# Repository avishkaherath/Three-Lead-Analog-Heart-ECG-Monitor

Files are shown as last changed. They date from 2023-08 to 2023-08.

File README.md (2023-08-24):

# Three-Lead-Analog-Heart-ECG-Monitor
A heart ECG monitor is a device that provides real-time electrical measurements of the heart's activity, aiding in diagnosing cardiac conditions like arrhythmias. This non-invasive method utilizes a 3-lead ECG signal acquired through electrodes placed on the left shoulder, right shoulder, and lower left abdomen. To enhance signal quality, noise reduction is performed using an instrumentation amplifier. Additionally, interference from 50Hz power supply noise is mitigated using a notch filter.

After noise reduction, the signal undergoes further refinement through a low-pass filter (cut-off frequency: 150Hz) and a high-pass filter (cut-off frequency: 0.05Hz). These filters isolate the essential cardiac signal while eliminating unwanted frequencies. The resulting filtered ECG signal is then amplified and displayed on an oscilloscope, enabling healthcare professionals to observe the heart's electrical activity.

## ECG Monitor
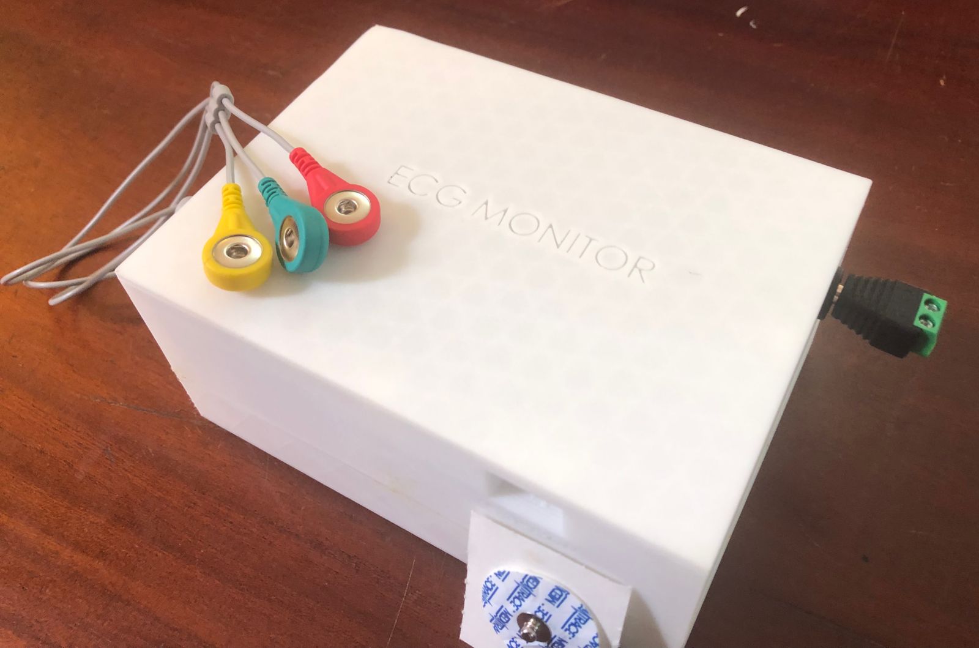
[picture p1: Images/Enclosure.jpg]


## Output ECG Waveform
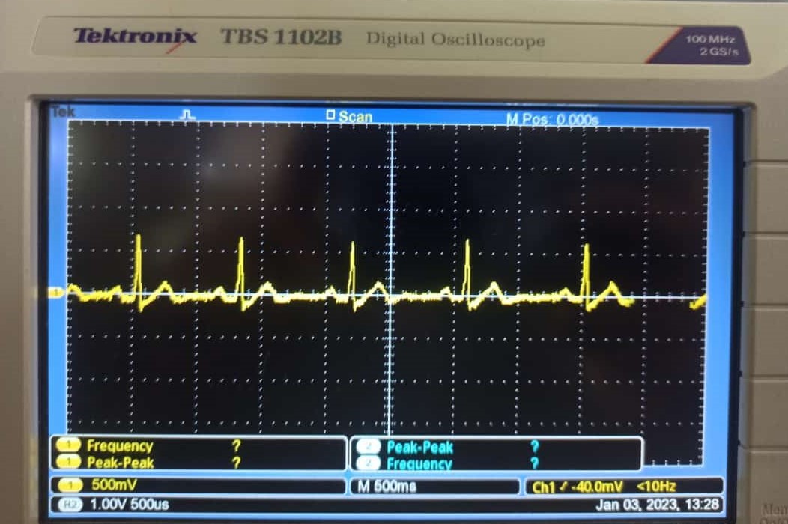
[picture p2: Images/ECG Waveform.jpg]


## Internal View
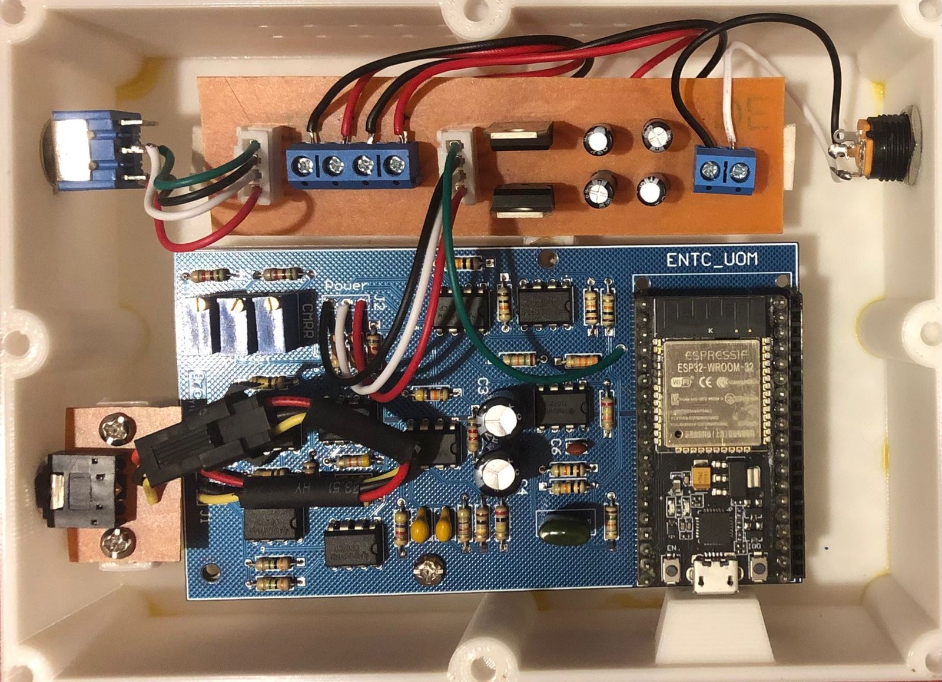
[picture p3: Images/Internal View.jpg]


## PCB Design
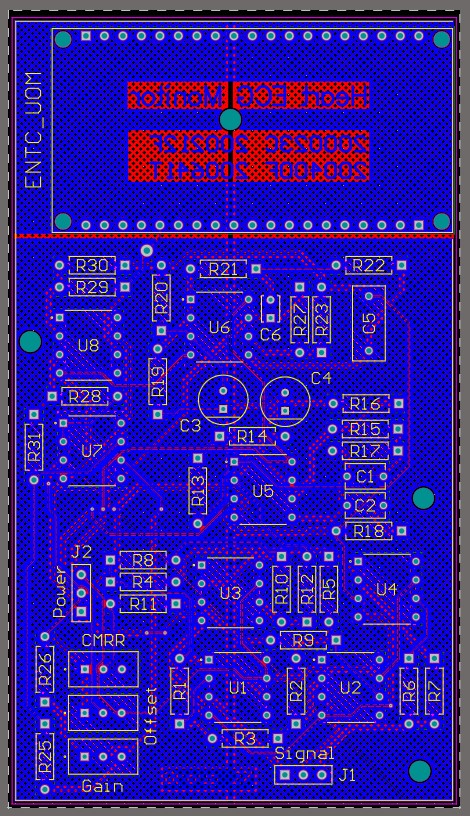
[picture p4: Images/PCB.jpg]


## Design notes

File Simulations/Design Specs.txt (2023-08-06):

Filter		Lower cutoff		Upper cutoff		Gain				Order

Notch			39.941 Hz			62.0634 Hz			1				2

HPF			68.3582 mHz			-				1				2

LPF			-				147.678 Hz			2				2

%%%%%%%%%%%%%%%%%%%%%%%%%%%%%%%%%%%%%%%%%%%%%%%%%%%%%%%%%%%%%%%%%%%%%%%%%%%%%%%%%%%%%%%%%%%%%%%%%%%%%%%%%%%%%%%%%%%%%%%%%%%%%%%%%%%%%%

Instrumentation Differential Mode						110

Instrumentation Common Mode							2.38407e-006

Summing Amplifier							min - 1.04853	max - 21.603

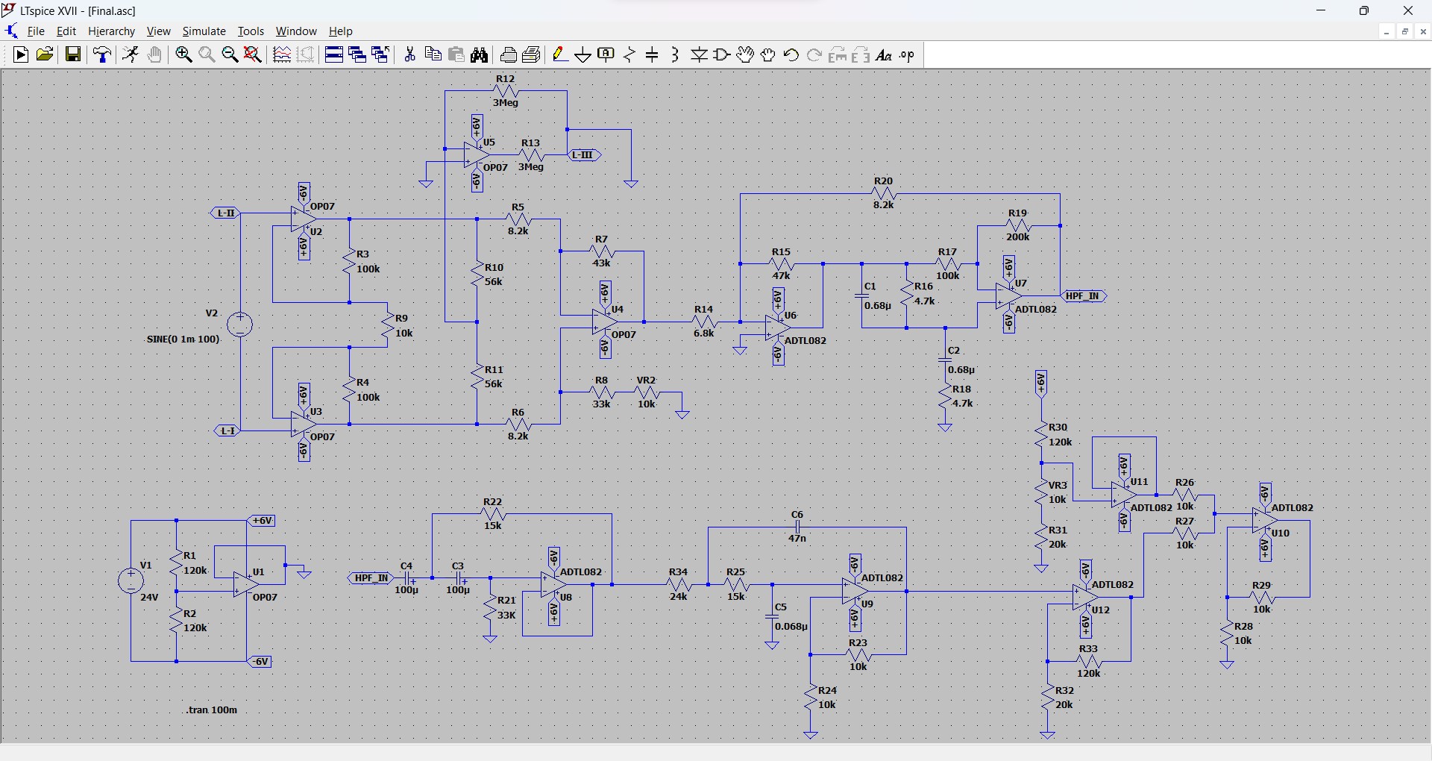
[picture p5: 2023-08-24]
Images/Schematic.jpg

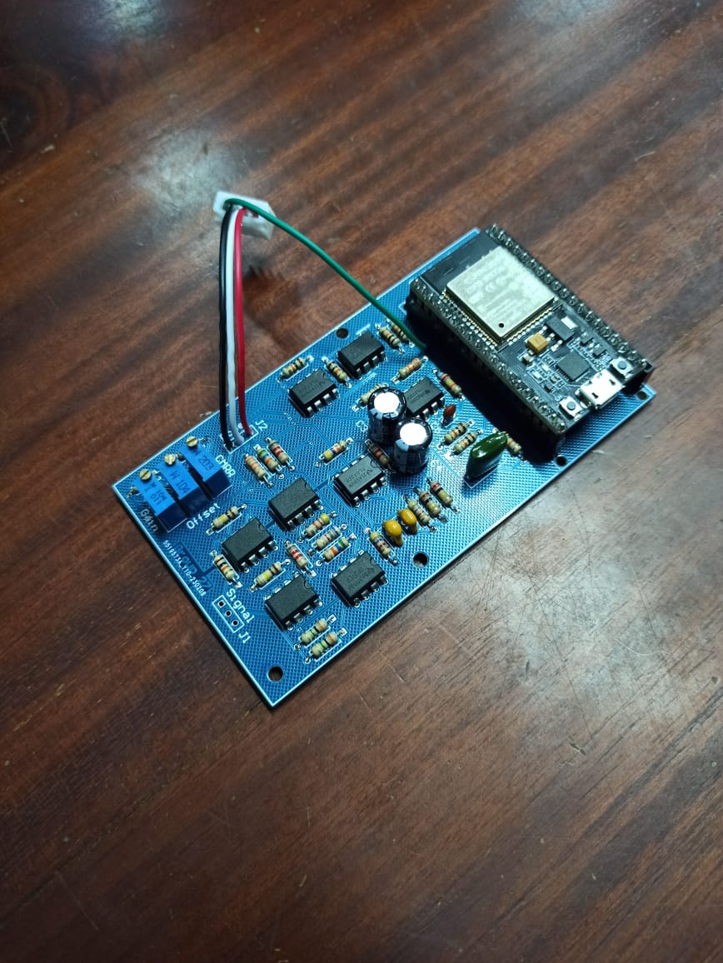
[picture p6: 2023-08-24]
Images/Final PCB.jpg

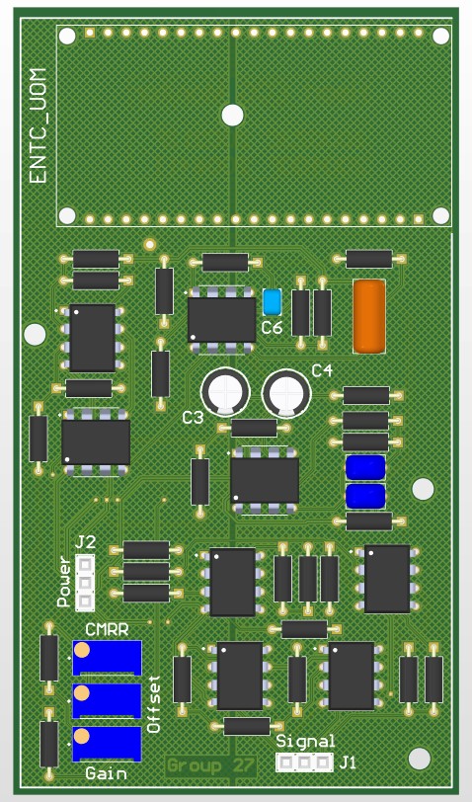
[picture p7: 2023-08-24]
Images/PCB_3D.jpg

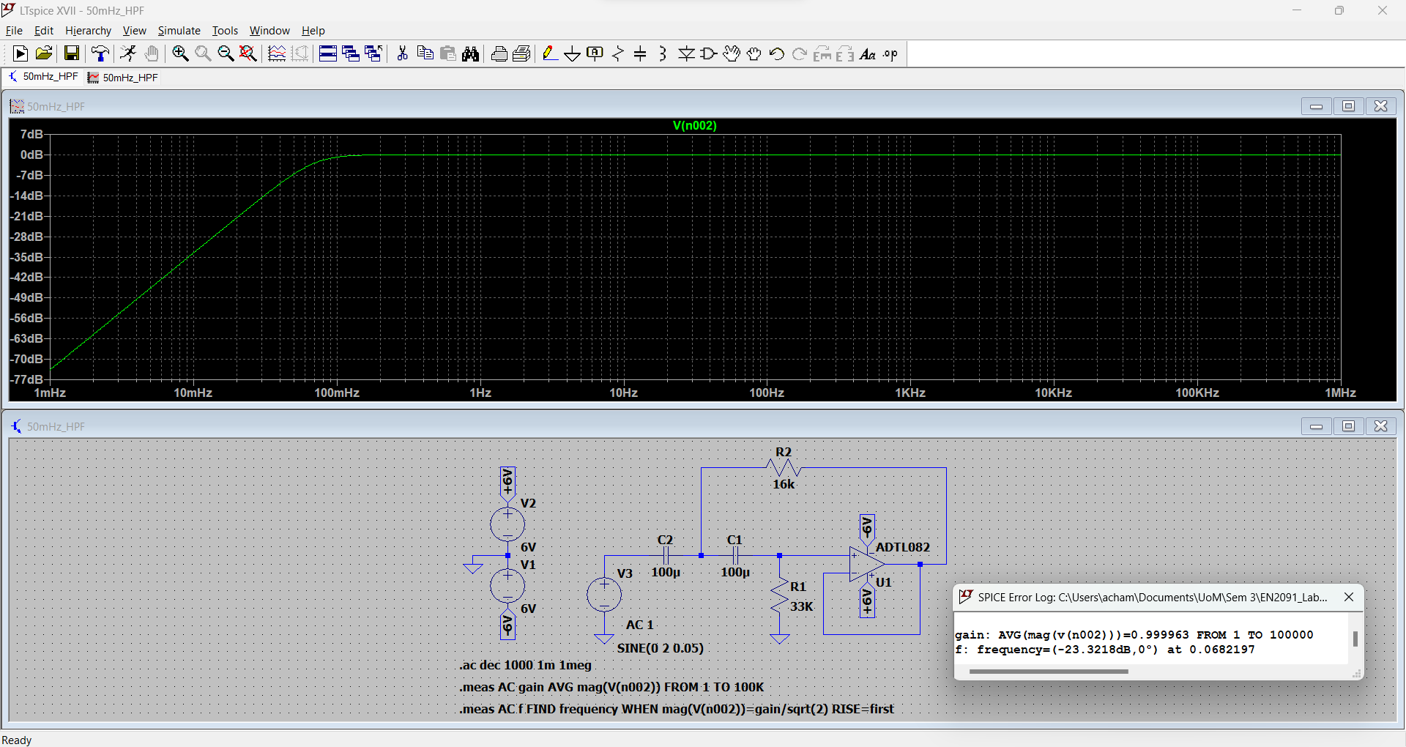
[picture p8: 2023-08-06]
Simulations/Screenshots/HPF.png

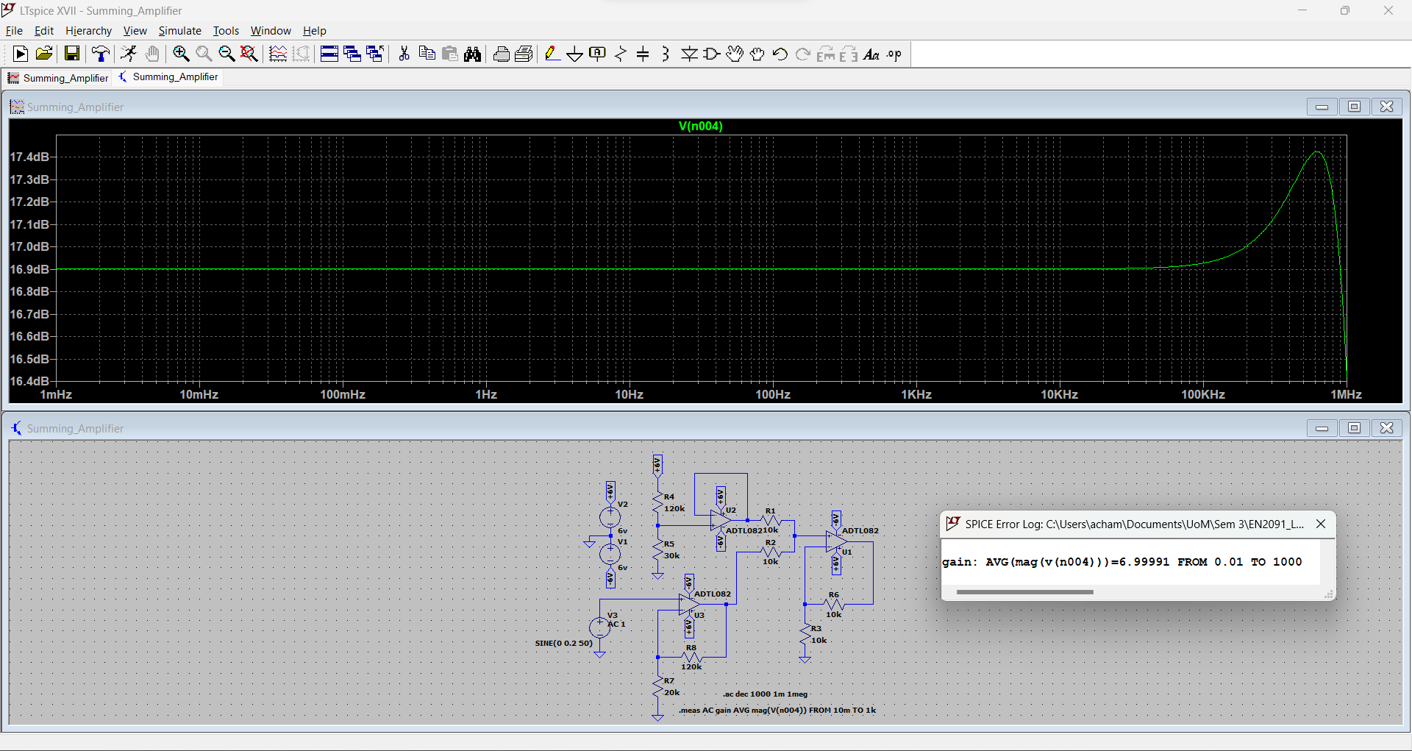
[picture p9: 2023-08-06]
Simulations/Screenshots/Summing_Amplifier.png

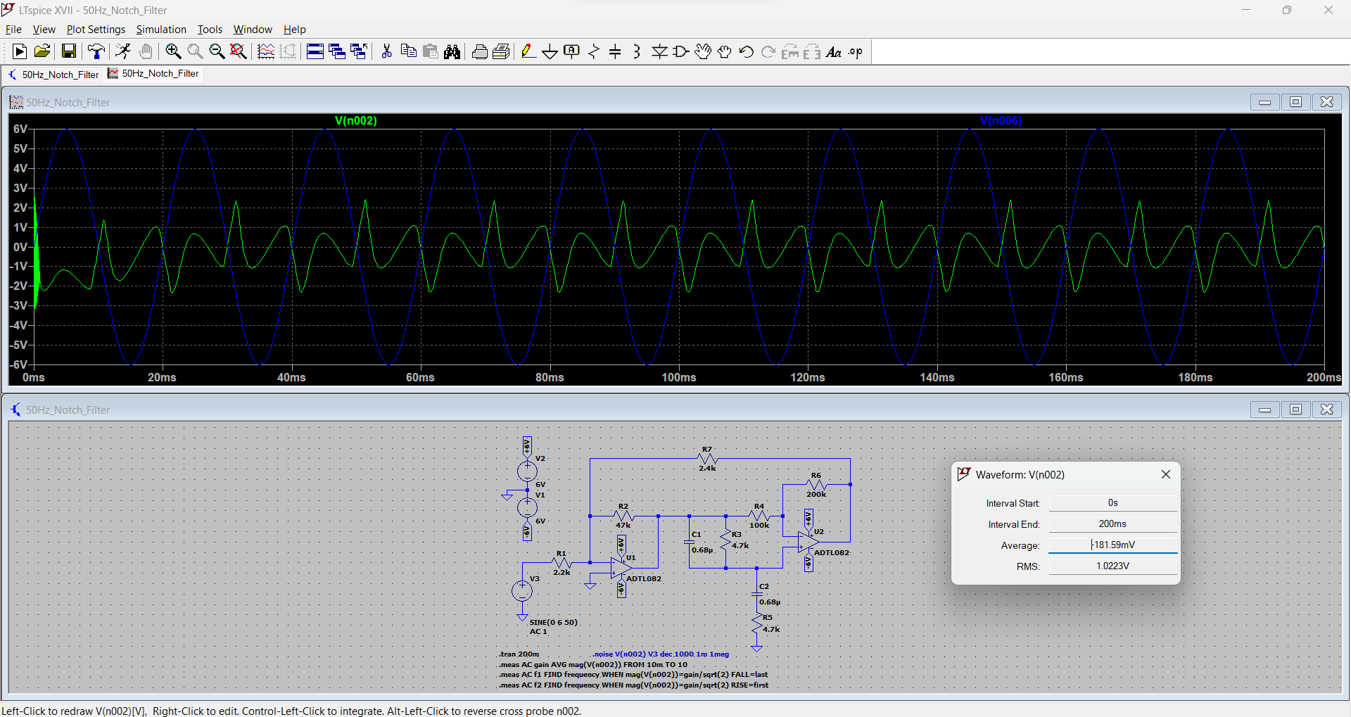
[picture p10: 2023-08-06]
Simulations/Screenshots/Notch_Filter_6V.png

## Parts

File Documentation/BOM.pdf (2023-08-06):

## Heart ECG Monitor Group 27

## BILL OF MATERIAL

Item | Quantity | Price (Rs.)
Resistors | 85 | 325.00
Capacitors | 10 | 253.50
Potentiometer | 1 | 142.00
Breadboard | 2 | 980.00
Variable Resistor | 1 | 50.00
40 pin Male Headers | 1 | 230.00
Rocker Switch | 1 | 18.00
Heat Shrink Tube | 1 | 24.00
Toggle Switch | 1 | 100.00
Connectors | | 350.00
OpAmp | 8 | 745.00
PCB | 3 | 4350.00
ECG Sensor | 1 | 1800.00
Audio Jack | 1 | 100.00
Wire Kit | 1 | 500.00
Enclosure | 1 | 8850.00
Screws | 15 | 75.00
Total | | 18892.50

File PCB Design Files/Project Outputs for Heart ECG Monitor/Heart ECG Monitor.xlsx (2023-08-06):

Comment | Description | Designator | Footprint | LibRef | Quantity
0.68uF |  | C1, C2 | CAPRB500W50L550T350H600 | FA26NP02J472JNU06 | 2
100uF | Cap Aluminum Lytic 100uF 25V 20% (6.3 X 11.2mm) Radial 2.5mm 130mA 1000h 105°C Ammo Pack | C3, C4 | FP-RAD-TH-D_6_3_0_5-L_11-MFG | CMP-001-00083-1 | 2
68nF |  | C5 | CAPRR750W60L1030T450H750 | ECQE2683JF | 1
47nF | Cap Ceramic 470pF 50V C0G 5% Radial 2.5mm 125°C Ammo Pack | C6 | FP-RCE0DB-MFG | CMP-001-00084-1 | 1
10uF | Cap Aluminum Lytic 100uF 25V 20% (6.3 X 11.2mm) Radial 2.5mm 130mA 1000h 105°C Ammo Pack | CM1, CM3 | FP-RAD-TH-D_6_3_0_5-L_11-MFG | CMP-001-00083-1 | 2
1uF | Cap Aluminum Lytic 100uF 25V 20% (6.3 X 11.2mm) Radial 2.5mm 130mA 1000h 105°C Ammo Pack | CM2, CM4 | FP-RAD-TH-D_6_3_0_5-L_11-MFG | CMP-001-00083-1 | 2
SIGNAL_IN | Low Profile Socket Strips, Through-hole, Vertical, -55 to 125 degC, 2.54 mm Pitch, 3-Pin, Female, RoHS | J1 | SMTC-SLW-103-01-X-S | CMP-1023-00128-1 | 1
POWER_IN | Low Profile Socket Strips, Through-hole, Vertical, -55 to 125 degC, 2.54 mm Pitch, 3-Pin, Female, RoHS | J2 | SMTC-SLW-103-01-X-S | CMP-1023-00128-1 | 1
3.5mm JACK | Conn 3.5MM Stereo Jack F 5 POS Solder RA Thru-Hole 5 Terminal 1 Port | Jin1 | SWITCHCRAFT_35RAPC4BHN2 | 35RAPC4BHN2 | 1
SIGNAL | Low Profile Socket Strips, Through-hole, Vertical, -55 to 125 degC, 2.54 mm Pitch, 3-Pin, Female, RoHS | Jin2 | SMTC-SLW-103-01-X-S | CMP-1023-00128-1 | 1
BATTERY |  | JM1 | CUI_TB001-500-04BE | TB001-500-04BE | 1
SWITCH | Low Profile Socket Strips, Through-hole, Vertical, -55 to 125 degC, 2.54 mm Pitch, 4-Pin, Female, RoHS | JM2 | SMTC-SLW-104-01-X-S | CMP-1023-00130-1 | 1
MAIN | Low Profile Socket Strips, Through-hole, Vertical, -55 to 125 degC, 2.54 mm Pitch, 4-Pin, Female, RoHS | JM3 | SMTC-SLW-104-01-X-S | CMP-1023-00130-1 | 1
OSCILLOSCOPE |  | JM4 | CUI_TB001-500-02BE | TB001-500-02BE | 1
100k | Axial Resistor, 100 KOhm, +/- 1%, 0.25 W, -55 to 155 degC, 2-Pin THD, RoHS, Bulk, Axial Resistor, 47.5 Ohm, +/- 1%, 0.25 W, -55 to 155 degC, 2-Pin THD, RoHS, Bulk | R1, R2, R15 | RESA60-630X240 | CMP-009-00045-4, CMP-009-00058-4 | 3
10k | Axial Resistor, 10 KOhm, +/- 1%, 0.25 W, -55 to 155 degC, 2-Pin THD, RoHS, Bulk | R3, R23, R27, R28, R29, R30, R31 | RESA60-630X240 | CMP-009-00047-4 | 7
56k | Axial Resistor, 47.5 KOhm, +/- 1%, 0.25 W, -55 to 155 degC, 2-Pin THD, RoHS, Bulk | R4, R5 | RESA60-630X240 | CMP-009-00057-4 | 2
3M | Axial Resistor, 1 MOhm, +/- 1%, 250 mW, -55 to 155 degC, 2-Pin THD, RoHS, Bulk | R6, R7 | RESA60-630X240 | CMP-009-00049-4 | 2
8.2k | Axial Resistor, 4.75 KOhm, +/- 1%, 0.25 W, -55 to 155 degC, 2-Pin THD, RoHS, Bulk, Axial Resistor, 47.5 Ohm, +/- 1%, 0.25 W, -55 to 155 degC, 2-Pin THD, RoHS, Bulk | R8, R9, R14 | RESA60-630X240 | CMP-009-00059-4, CMP-009-00058-4 | 3
43k | Axial Resistor, 47.5 KOhm, +/- 1%, 0.25 W, -55 to 155 degC, 2-Pin THD, RoHS, Bulk | R10 | RESA60-630X240 | CMP-009-00057-4 | 1
33k | Axial Resistor, 47.5 KOhm, +/- 1%, 0.25 W, -55 to 155 degC, 2-Pin THD, RoHS, Bulk, Axial Resistor, 47.5 Ohm, +/- 1%, 0.25 W, -55 to 155 degC, 2-Pin THD, RoHS, Bulk | R11, R20 | RESA60-630X240 | CMP-009-00057-4, CMP-009-00058-4 | 2
6.8k | Axial Resistor, 47.5 Ohm, +/- 1%, 0.25 W, -55 to 155 degC, 2-Pin THD, RoHS, Bulk | R12 | RESA60-630X240 | CMP-009-00058-4 | 1
47k | Axial Resistor, 47.5 Ohm, +/- 1%, 0.25 W, -55 to 155 degC, 2-Pin THD, RoHS, Bulk | R13 | RESA60-630X240 | CMP-009-00058-4 | 1
200k | Axial Resistor, 47.5 Ohm, +/- 1%, 0.25 W, -55 to 155 degC, 2-Pin THD, RoHS, Bulk | R16 | RESA60-630X240 | CMP-009-00058-4 | 1
4.7k | Axial Resistor, 47.5 Ohm, +/- 1%, 0.25 W, -55 to 155 degC, 2-Pin THD, RoHS, Bulk | R17, R18 | RESA60-630X240 | CMP-009-00058-4 | 2
15k | Axial Resistor, 47.5 Ohm, +/- 1%, 0.25 W, -55 to 155 degC, 2-Pin THD, RoHS, Bulk, Axial Resistor, 10 KOhm, +/- 1%, 0.25 W, -55 to 155 degC, 2-Pin THD, RoHS, Bulk | R19, R22 | RESA60-630X240 | CMP-009-00058-4, CMP-009-00047-4 | 2
24k | Axial Resistor, 10 KOhm, +/- 1%, 0.25 W, -55 to 155 degC, 2-Pin THD, RoHS, Bulk | R21 | RESA60-630X240 | CMP-009-00047-4 | 1
5.1k | Axial Resistor, 10 KOhm, +/- 1%, 0.25 W, -55 to 155 degC, 2-Pin THD, RoHS, Bulk | R25, R26 | RESA60-630X240 | CMP-009-00047-4 | 2
OP07CP |  | U1, U2, U3, U4, U8 | DIP794W45P254L959H508Q8 | OP07CP | 5
TL072BCP | Dual low-noise JFET-input low offset operational amplifier 8-PDIP 0 to 70 | U5, U6, U7 | DIP794W45P254L959H508Q8 | CMP-005-000000-1 | 3
ESP32_NODEMCU |  | U9 | MODULE_ESP32_NODEMCU | ESP32_NODEMCU | 1
LM7806CT | Positive Voltage Regulator, 6V, 3-Pin TO-220 | UM1, UM2 | TO220 | CMP-0244-00495-1 | 2
100k | Res Cermet Trimmer 500K Ohm 10% 0.5W 25(Elec)Turn 2.19mm (9.53 X 4.83 X 11.55mm) Pin Thru-Hole Tube | VR1, VR2 | TRIM_3296W-OT1-103 | 3296W-OT1-103 | 2
20k | Res Cermet Trimmer 500K Ohm 10% 0.5W 25(Elec)Turn 2.19mm (9.53 X 4.83 X 11.55mm) Pin Thru-Hole Tube | VR3 | TRIM_3296W-OT1-103 | 3296W-OT1-103 | 1

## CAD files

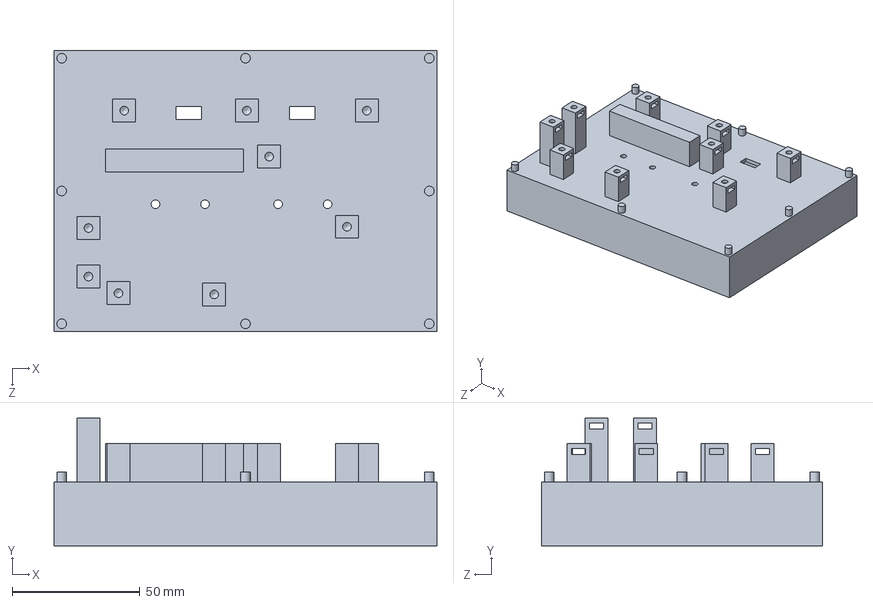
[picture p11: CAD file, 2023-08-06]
Enclosure Design/Final Assembly/Main.SLDPRT
150.0 x 50.0 x 110.0 mm

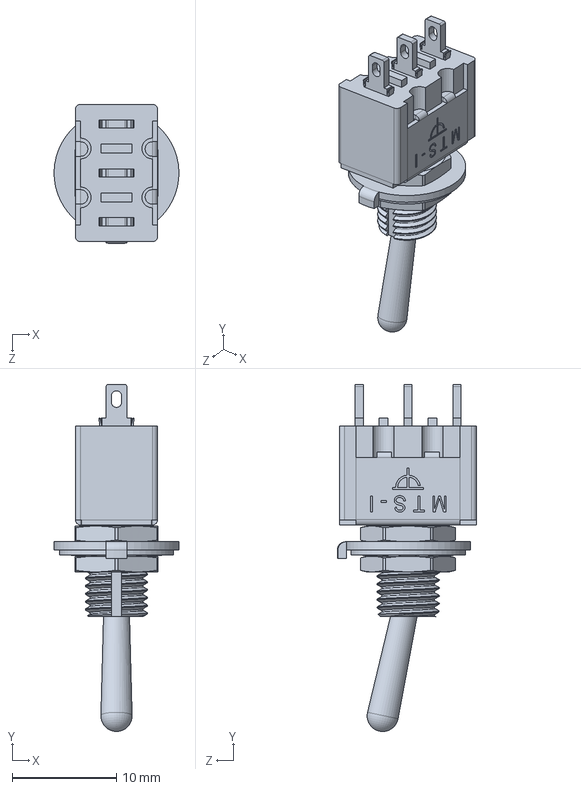
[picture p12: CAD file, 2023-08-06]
Enclosure Design/Final Assembly/Switch.SLDPRT
12.0 x 33.3 x 13.4 mm

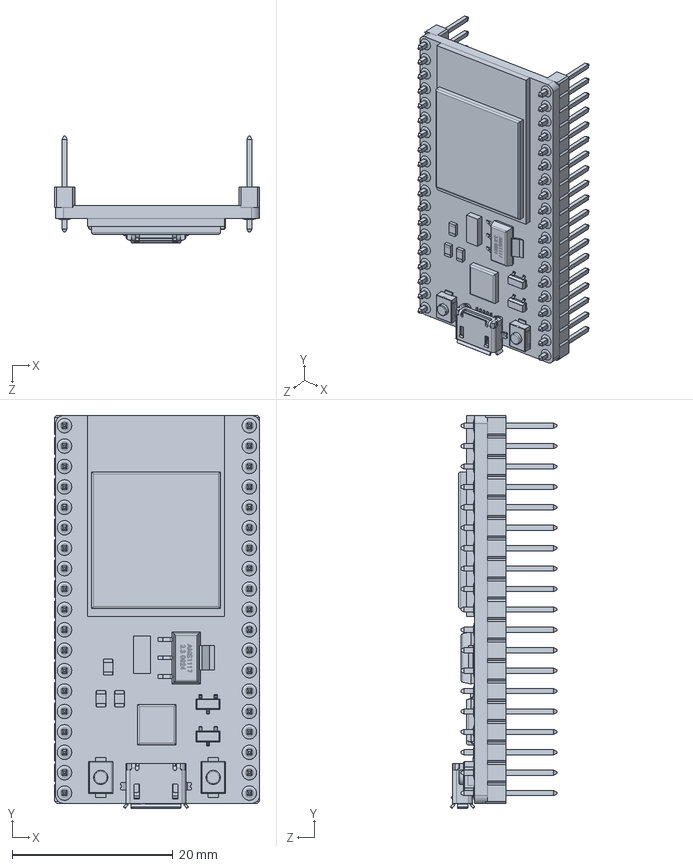
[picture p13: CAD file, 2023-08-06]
Enclosure Design/Part Files/NodeMCU.SLDPRT
25.5 x 48.9 x 13.3 mm

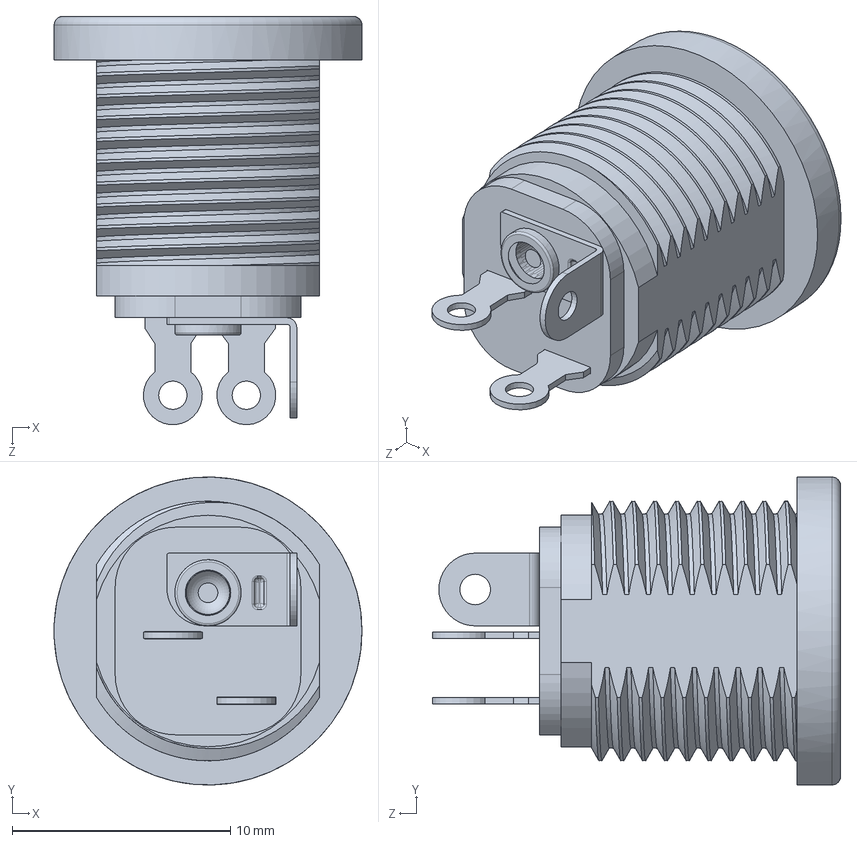
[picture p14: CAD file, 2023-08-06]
Enclosure Design/Final Assembly/Oscilloscope.SLDPRT
14.1 x 14.1 x 18.7 mm

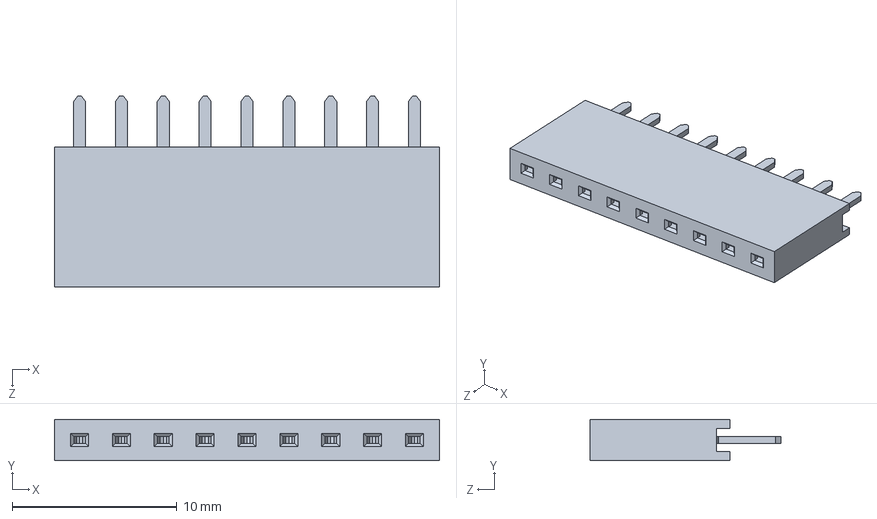
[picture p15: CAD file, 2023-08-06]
Enclosure Design/Part Files/9 Pin Header.SLDPRT
23.4 x 2.50 x 11.6 mm

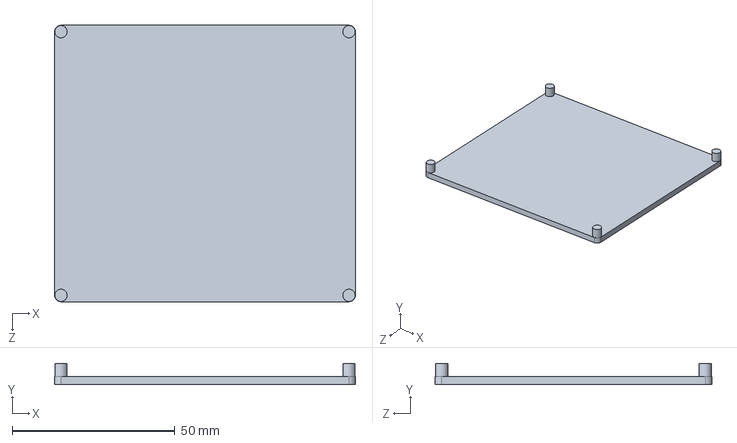
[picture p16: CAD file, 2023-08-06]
Enclosure Design/Final Assembly/Bottom.SLDPRT
92.5 x 6.50 x 85.0 mm

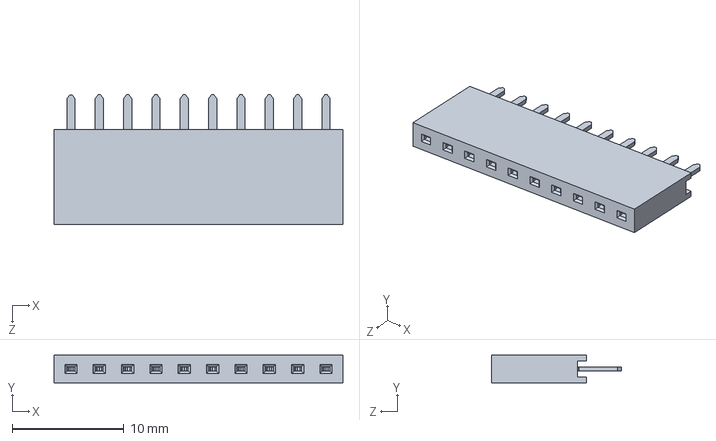
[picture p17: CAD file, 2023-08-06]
Enclosure Design/Part Files/10 Pin Header.SLDPRT
25.9 x 2.50 x 11.6 mm

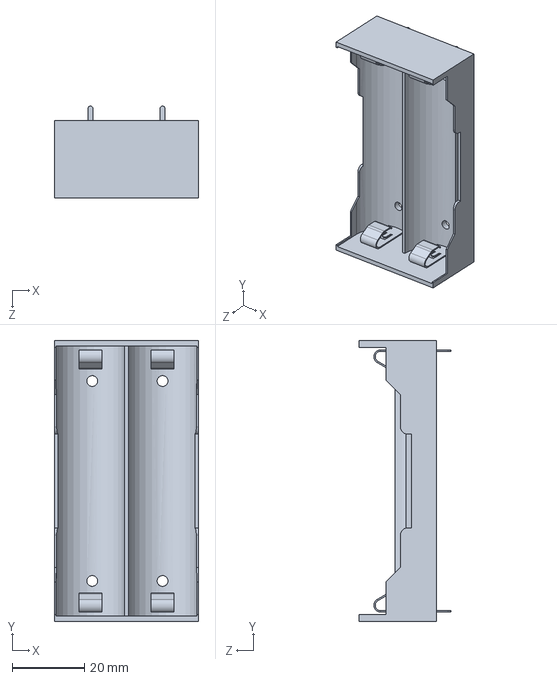
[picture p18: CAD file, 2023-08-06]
Enclosure Design/Part Files/Battery Holder.SLDPRT
40.0 x 78.0 x 25.5 mm

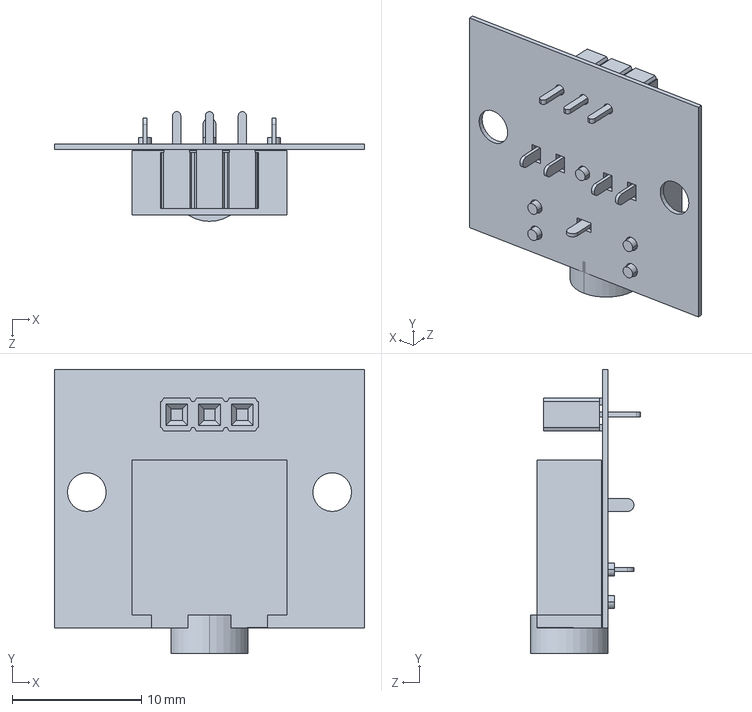
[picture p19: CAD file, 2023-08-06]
Enclosure Design/Final Assembly/PCB_Input.SLDPRT
24.0 x 22.0 x 8.50 mm

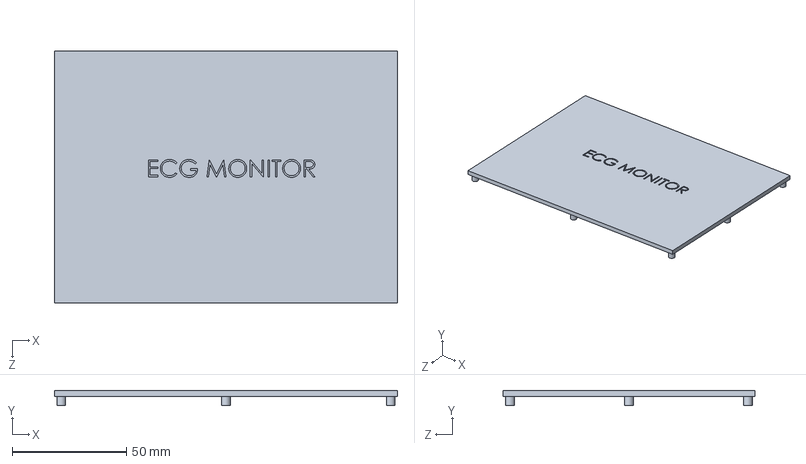
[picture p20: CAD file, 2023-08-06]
Enclosure Design/Final Assembly/Top.SLDPRT
150.0 x 6.50 x 110.0 mm

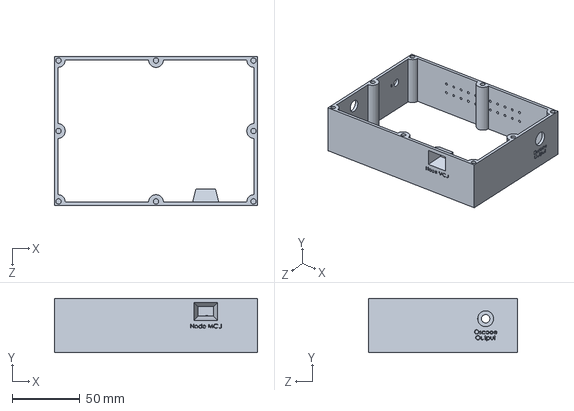
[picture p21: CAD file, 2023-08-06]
Enclosure Design/Final Assembly/Cover.SLDPRT
150.0 x 40.0 x 110.0 mm

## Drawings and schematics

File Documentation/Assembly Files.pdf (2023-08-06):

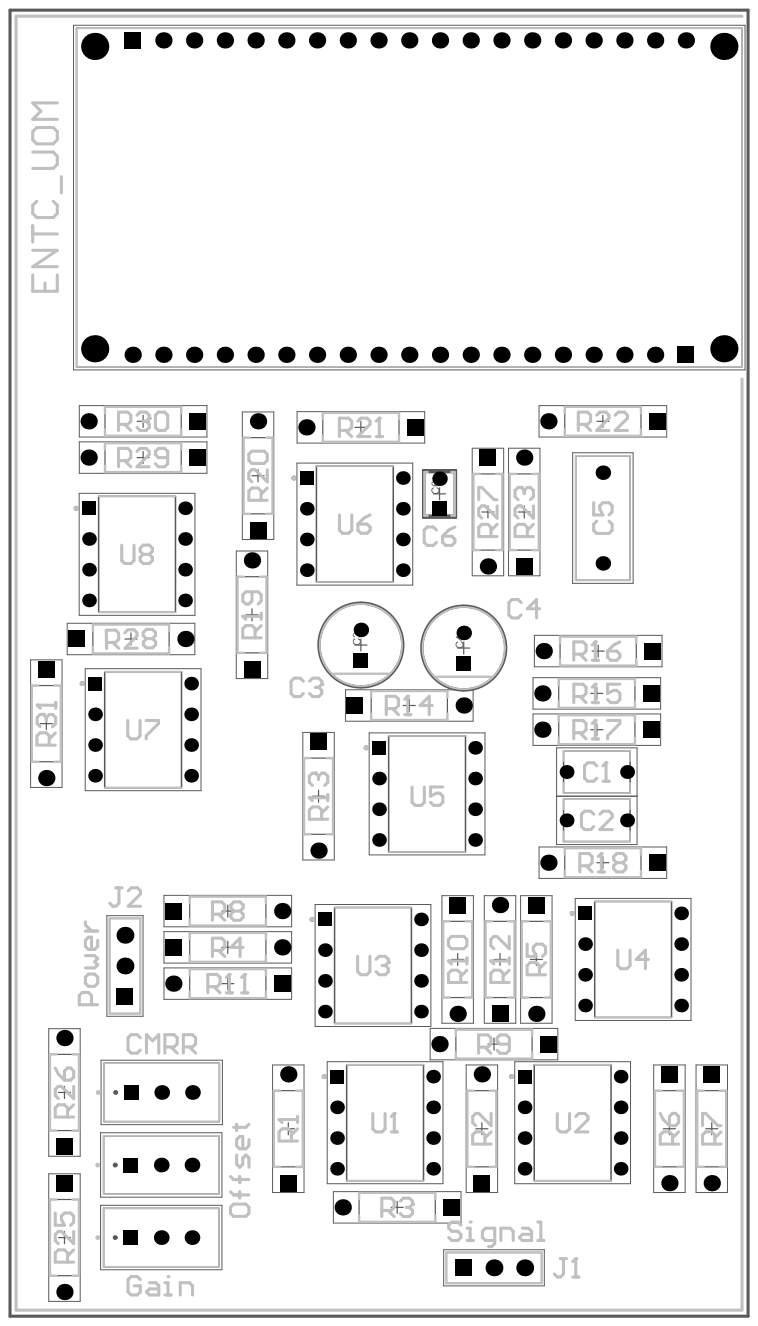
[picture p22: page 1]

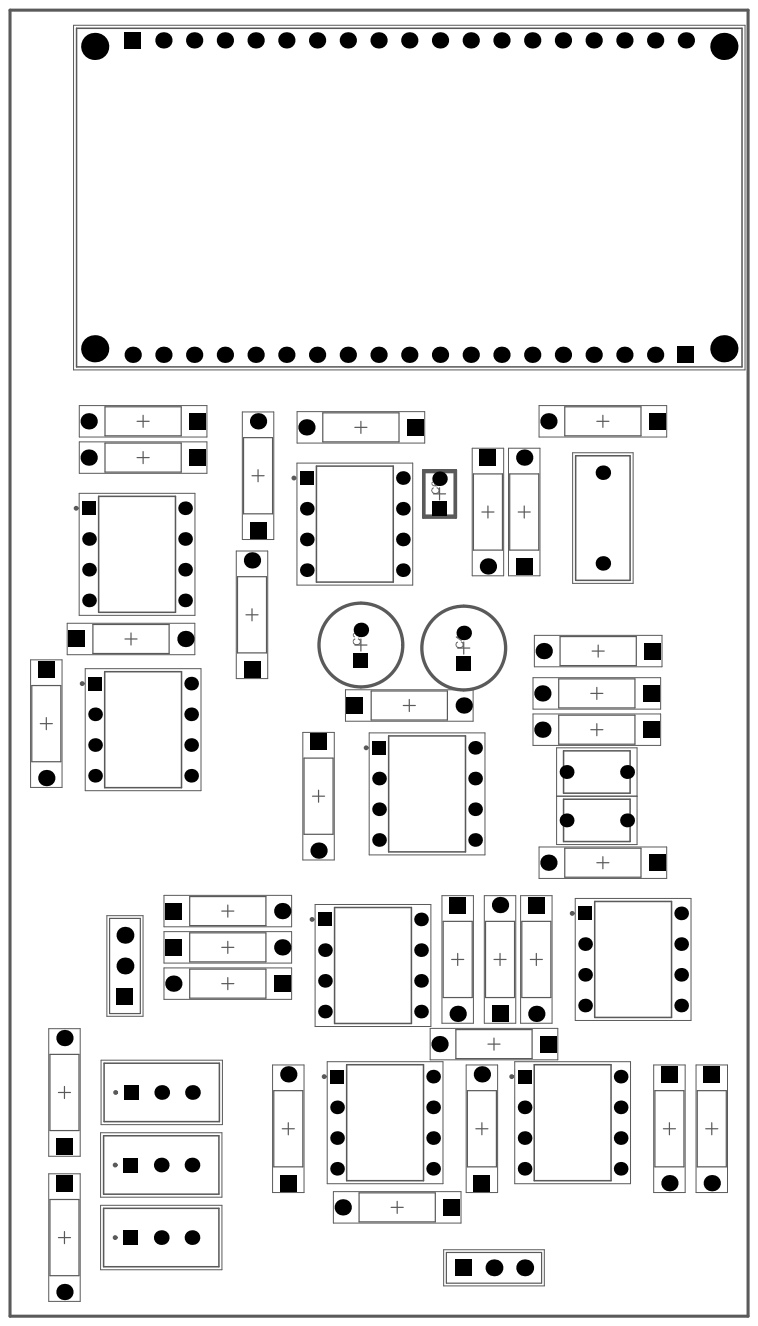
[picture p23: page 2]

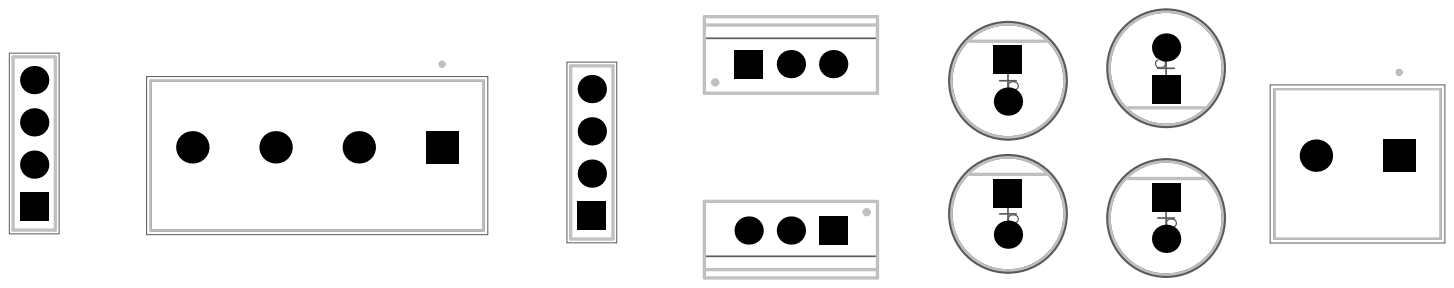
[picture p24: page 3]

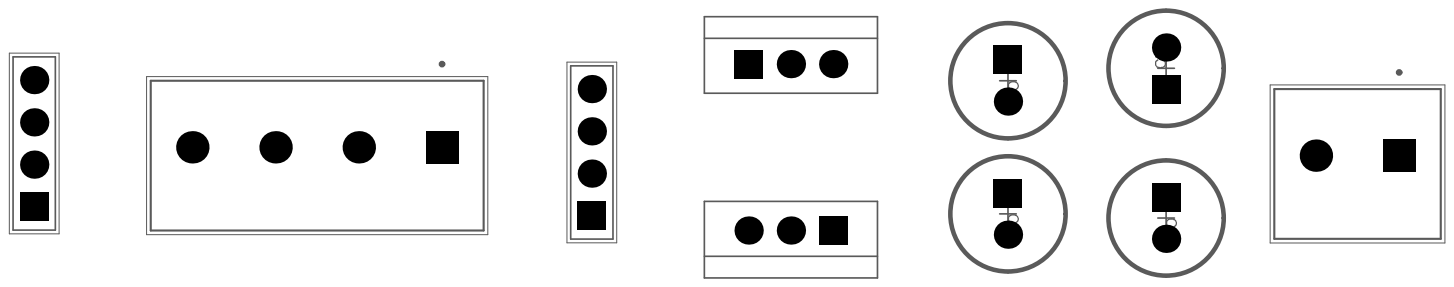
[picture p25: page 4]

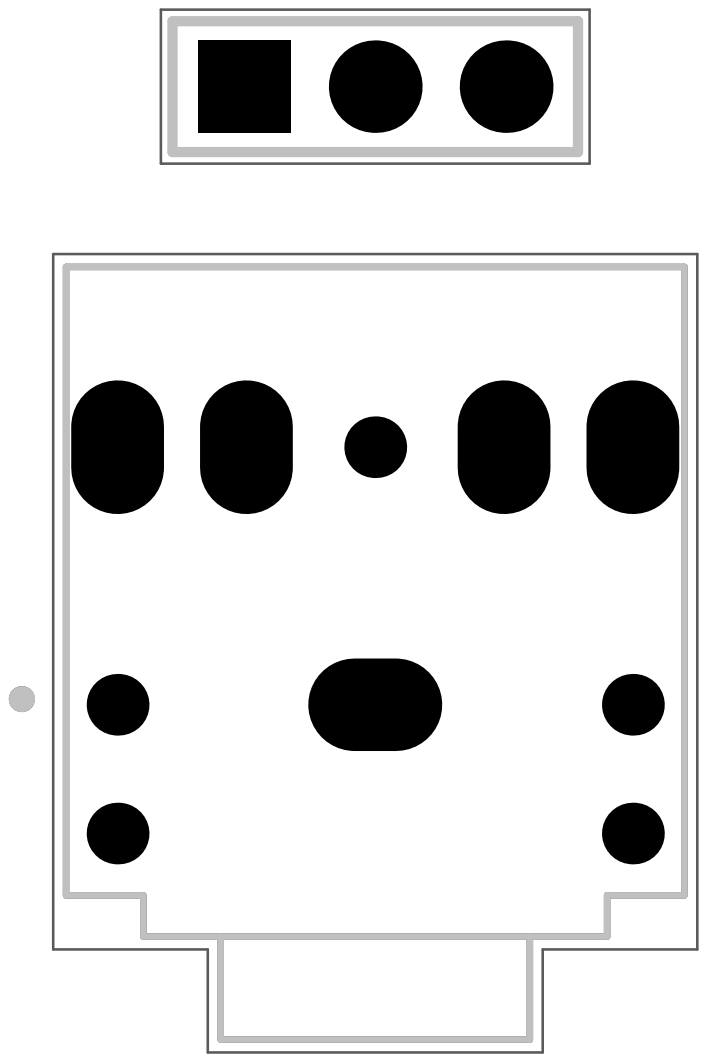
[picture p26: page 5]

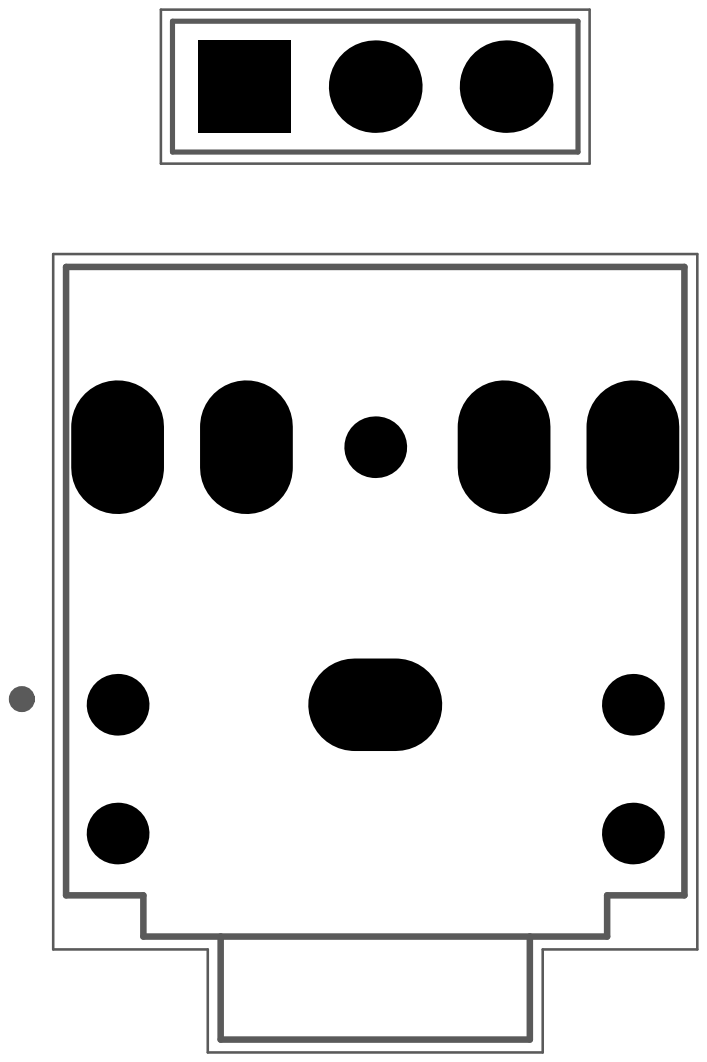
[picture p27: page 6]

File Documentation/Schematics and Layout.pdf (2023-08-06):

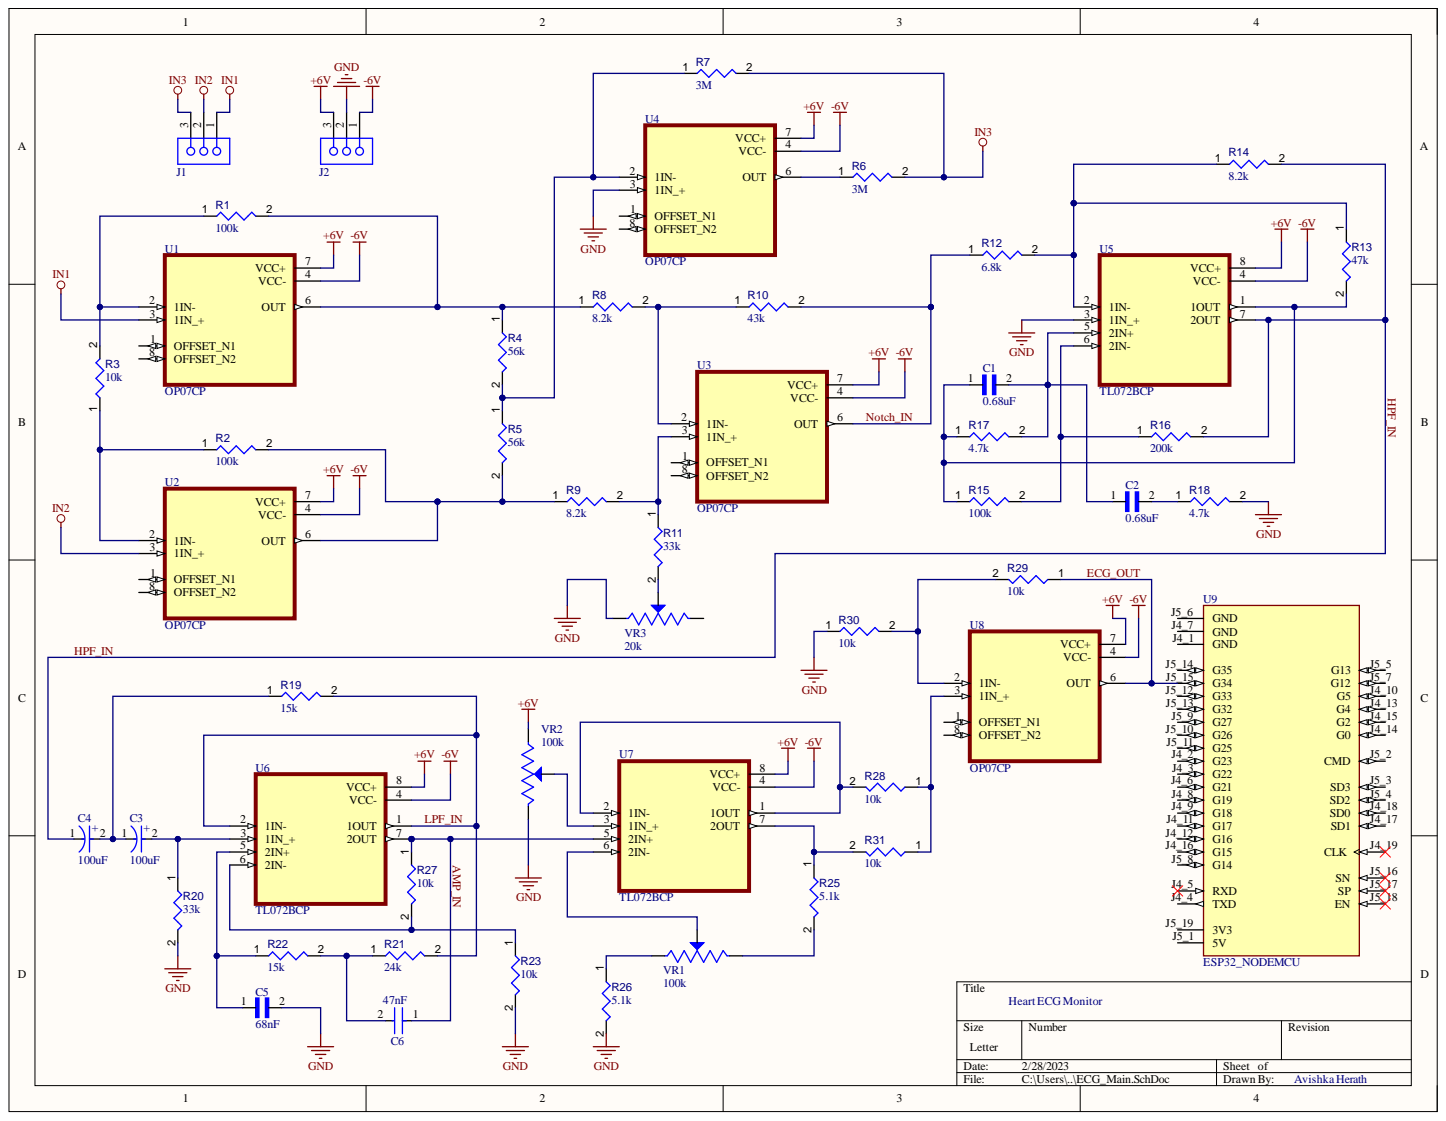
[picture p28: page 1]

OFFSET_N1 1

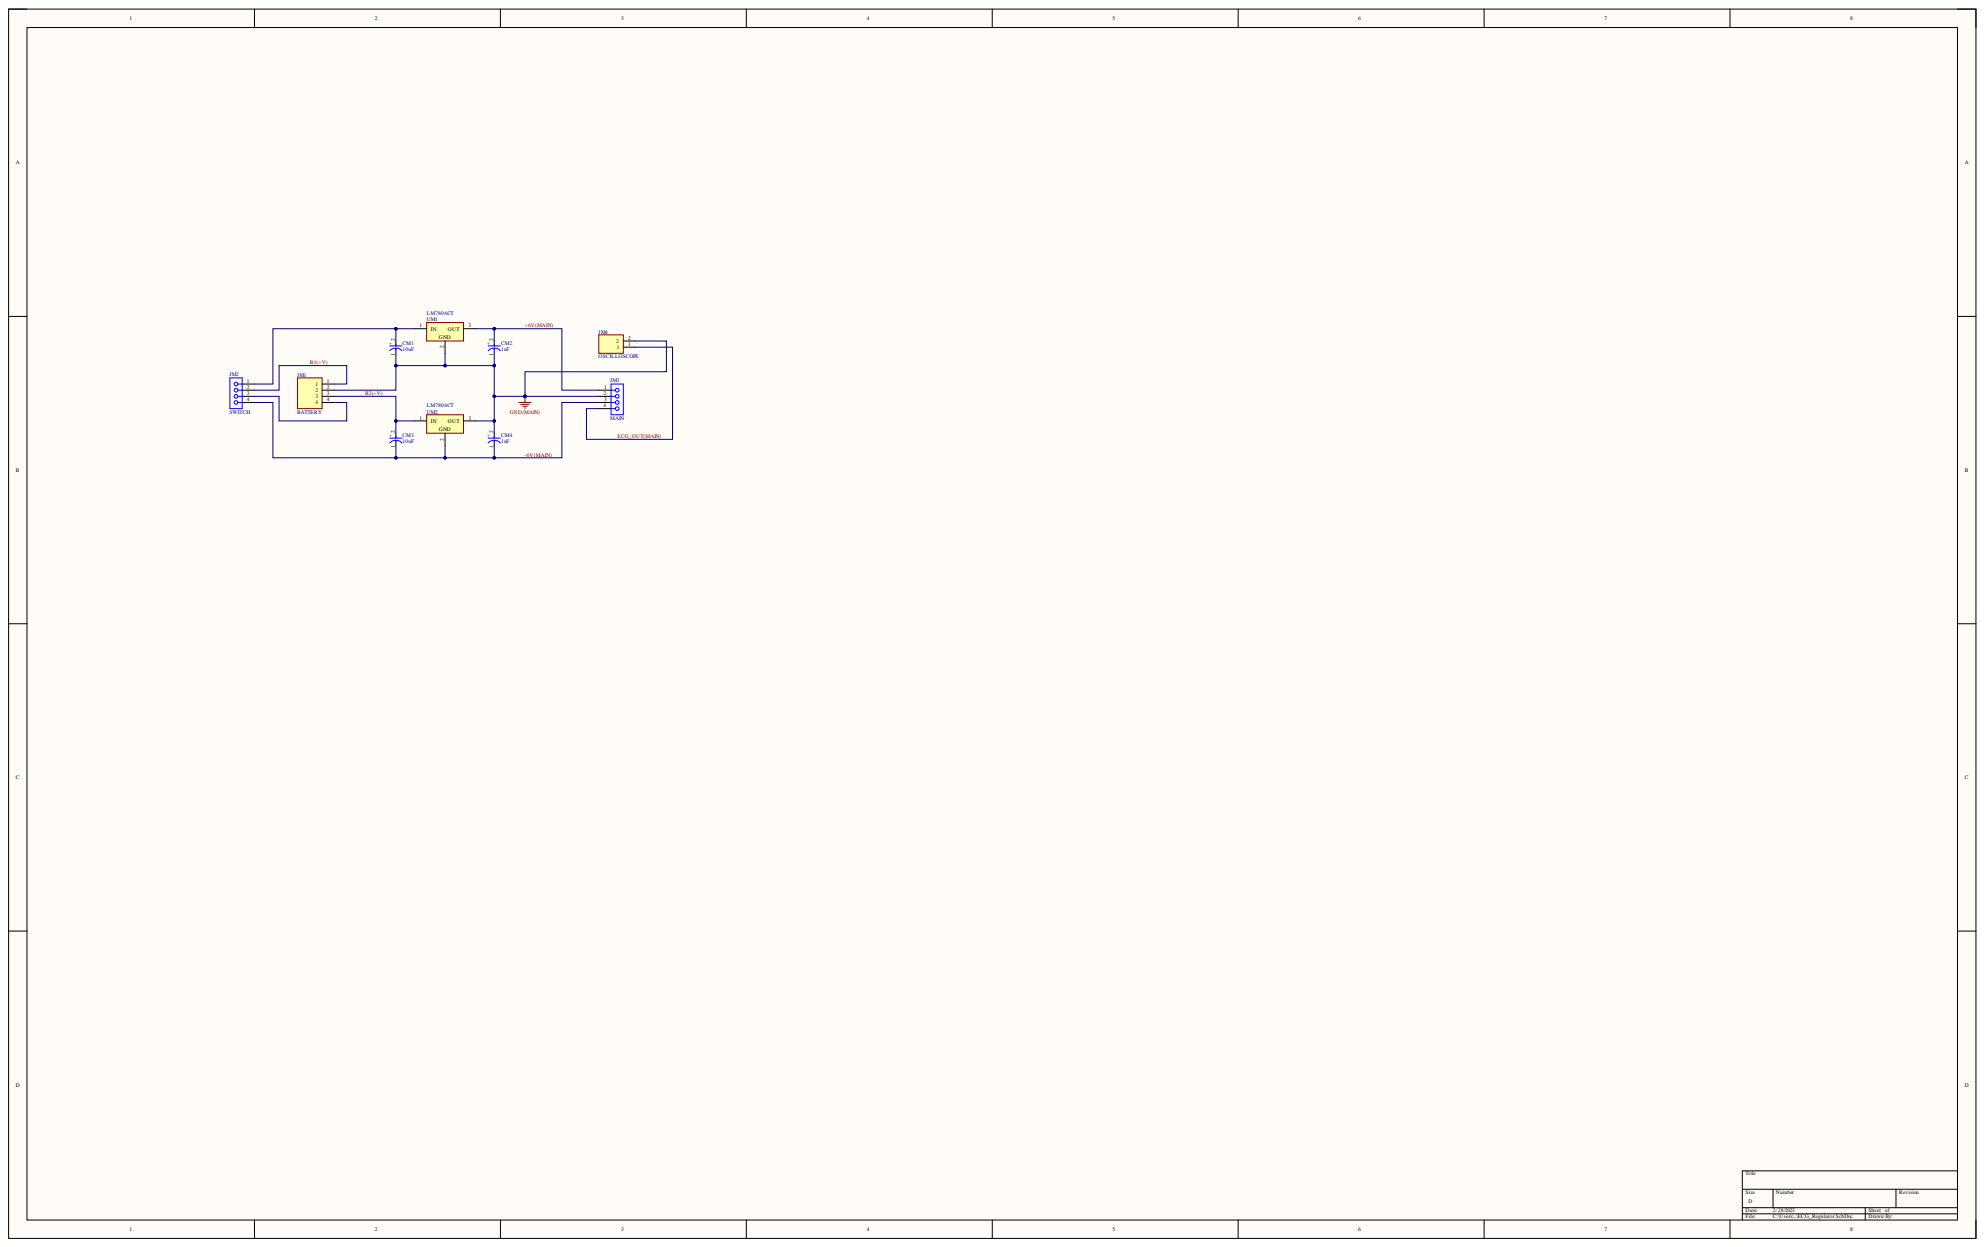
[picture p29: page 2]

B1(+V ) | J M4 OSCIL 2

1 L J M3 | 1 OSCO PE

Size DDat | N umb er | Rev i s ion

e: 2 / 2 8 /202 3 Fi l e: C: \U sers \ . . \ECG _Reg u lat or.Sch D oc | Sheet o f Draw n By :

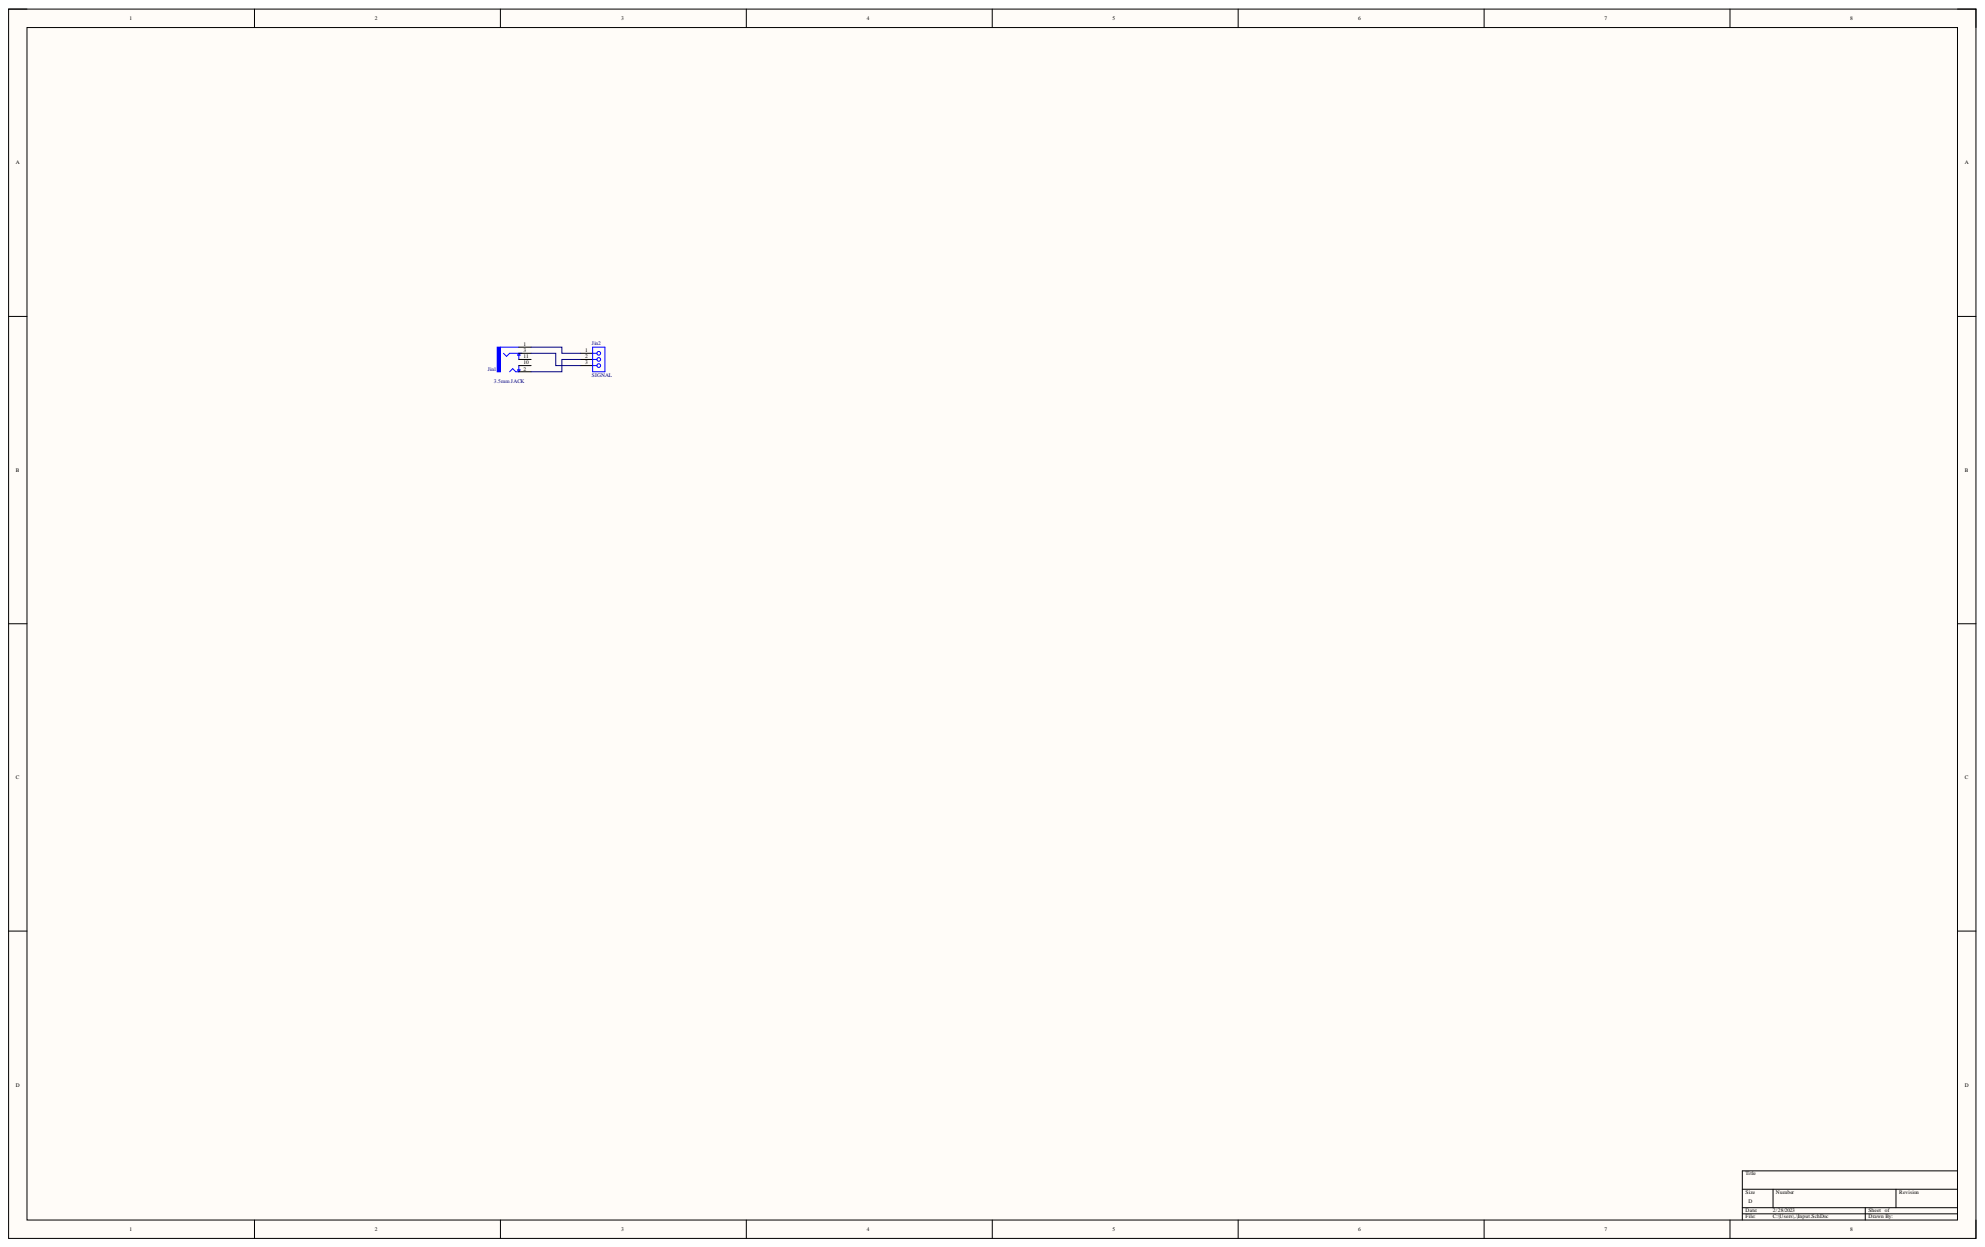
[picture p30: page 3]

Size DDat | N umb er | Rev i s ion

e: 2 / 2 8 /202 3 Fi l e: C: \U sers \ . . \In p u t .Sch D oc | Sheet o f Draw n By :

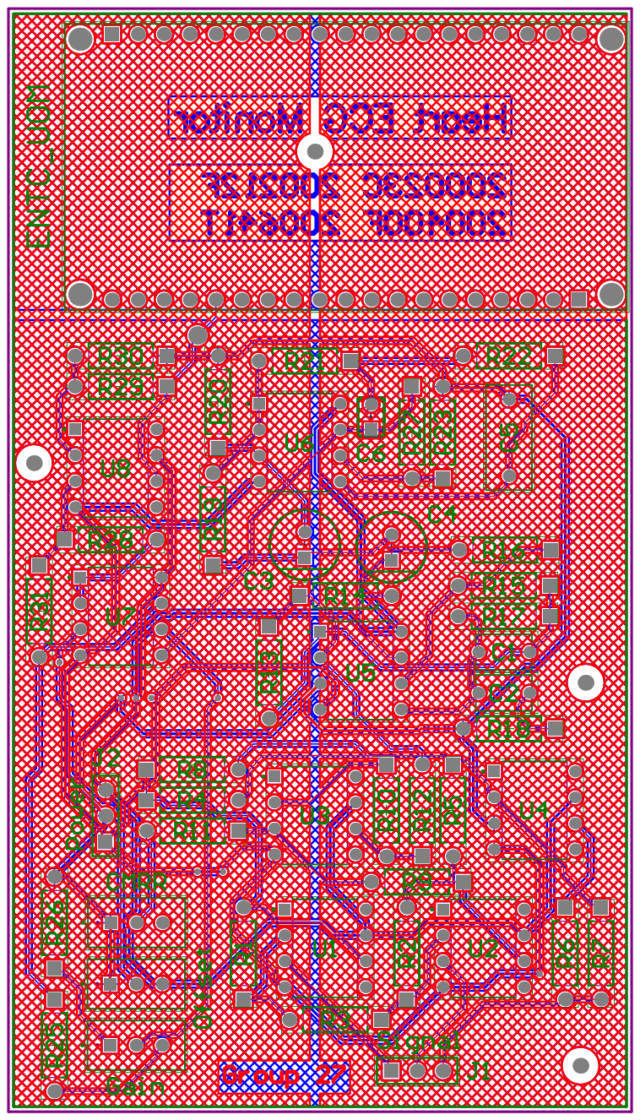
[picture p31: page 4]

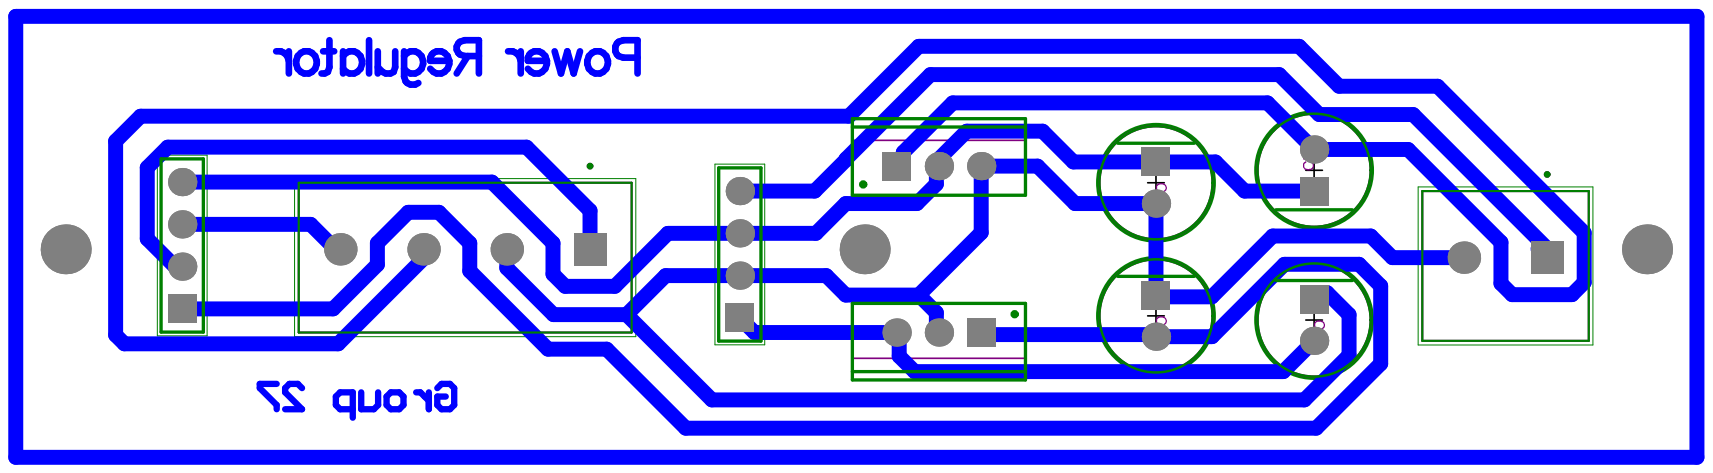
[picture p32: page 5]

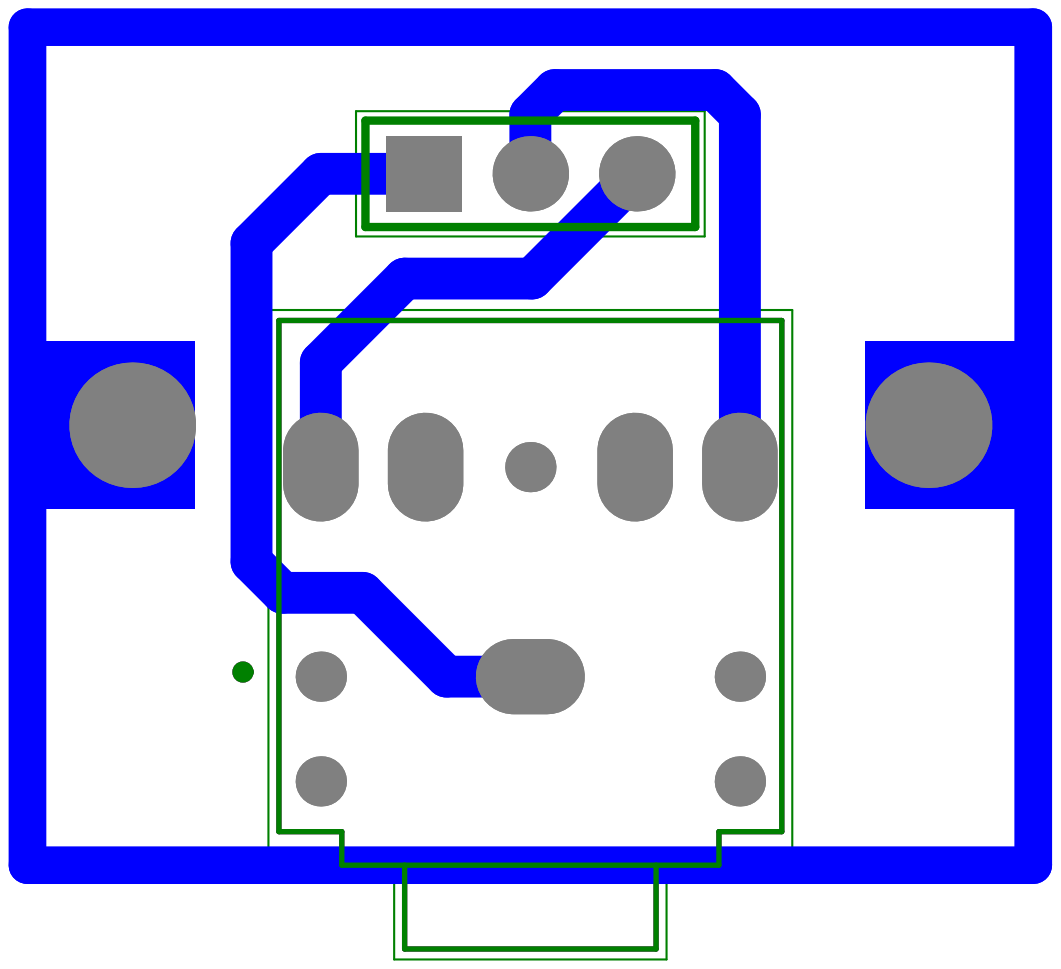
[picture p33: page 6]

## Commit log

2023-08-06 Included most of the design files
    [10 Pin Header.SLDPRT, 9 Pin Header.SLDPRT, Battery Holder.SLDPRT, Bottom.SLDPRT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]
2023-08-07 Updated a few files
    [ECG_Main.GBL, ECG_Main.GBO, ECG_Main.GBP, ECG_Main.GBS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]
